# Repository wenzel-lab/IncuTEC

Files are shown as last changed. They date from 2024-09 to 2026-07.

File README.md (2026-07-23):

# IncuTEC

IncuTEC is a custom microscope incubator that uses a thermoelectric
(Peltier) heating and cooling system with CO₂ control. It is designed for
the [SQUID microscope](https://github.com/wenzel-lab/SQUID-bioimaging-platform)
and other optical instruments with a similar footprint.

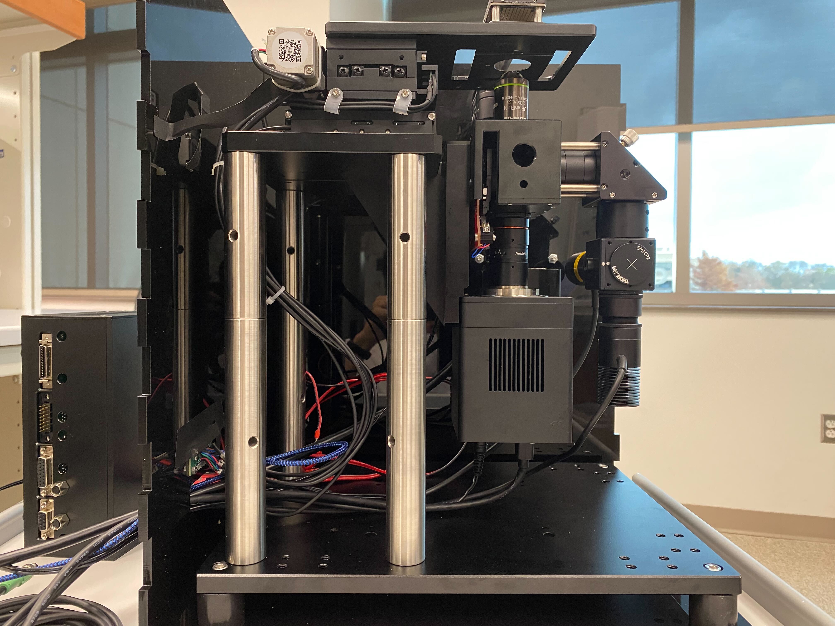
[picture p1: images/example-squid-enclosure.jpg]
IncuTEC enclosure around a SQUID microscope


## Documentation

### Start here

| Document | What it contains |
| --- | --- |
| [Assembly guide](assembly-guide.md) | Illustrated, step-by-step enclosure assembly instructions |
| [Bilingual assembly instructions (Word)](docs/incutec-assembly-instructions-bilingual.docx) | Spanish and English assembly instructions in a downloadable document |
| [Pneumatic system diagram](docs/incutec-pneumatic-system-diagram.pdf) | CO₂ tank, regulator, valves, gauges, and incubator connections |
| [UIM V2 user manual (English)](docs/uim-v2-user-manual-en.pdf) | Operation and configuration of the temperature controller display |
| [Temperature control module FAQ (English)](docs/tcm-temperature-control-module-faq-en.pdf) | Initial configuration and troubleshooting for the TCM controller |
| [UIM display module notes](docs/uim-display-module-notes.md) | Project-specific notes about language and maximum output voltage |

### Temperature-control references

- [TCM temperature control module overview (English)](docs/tcm-temperature-control-module-overview-en.pdf)
- [UIM universal display module overview (English)](docs/uim-universal-display-module-overview-en.pdf)
- [TCM parallel operation application note (English)](docs/tcm-parallel-operation-application-note-en.pdf)
- [Alternate translation of the TCM parallel operation application note](docs/tcm-parallel-operation-application-note-en-alternate.pdf)
- [Laird: heating and cooling of incubator chambers (2020)](docs/laird-incubator-heating-cooling-application-note-2020.pdf)
- [Laird SAA-170-24-22 thermoelectric cooler datasheet](docs/laird-saa-170-24-22-tec-datasheet.pdf)

### Sensor datasheets

- [Sensirion SCD30 CO₂, humidity, and temperature sensor](docs/SensorDatasheets/sensirion-scd30-co2-sensor-datasheet.pdf)
- [Winsen ME2-O2 oxygen sensor](docs/SensorDatasheets/winsen-me2-o2-sensor-manual.pdf)
- [Seeed Grove SHT35 temperature and humidity sensor](docs/SensorDatasheets/seeed-grove-sht35-temperature-humidity-sensor-datasheet.pdf)
- [Seeed Grove MQ2 gas sensor](docs/SensorDatasheets/seeed-grove-mq2-gas-sensor-datasheet.pdf)
- [Seeed Grove light sensor v1.2](docs/SensorDatasheets/seeed-grove-light-sensor-v1.2-datasheet.pdf)
- [Seeed Grove real-time clock](docs/SensorDatasheets/seeed-grove-rtc-user-manual.pdf)

## Wenzel Lab operating guide

> [!CAUTION]
> CO₂ can displace oxygen. Use the incubator only in a properly ventilated
> space, secure the gas cylinder, and follow your institution's compressed-gas
> safety procedures.

### Start-up

1. Check that the pneumatic connections are secure and that the run/vent valve
   on the incubator is in the correct position.
2. Switch on the mains power at the back of the controller. The Raman laser
   driver is powered by the same controller/power supply.
3. Set the target temperature and switch temperature control on using the UIM
   display (the white box with the round button).
4. Open the main valve on the CO₂ cylinder.
5. Move the gas-control slider on the controller to **HIGH**. The target CO₂
   percentage can currently be changed only in the microcontroller settings
   over USB.
6. Monitor temperature and CO₂ until both readings are stable before beginning
   an experiment.

### Shut-down

1. Close the main valve on the CO₂ cylinder; the regulator does not need to be
   adjusted.
2. Vent the remaining CO₂ using the run/vent valve near the incubator inlet.
3. Move the gas-control slider to **LOW**.
4. Switch temperature control off using the UIM display.
5. Turn off the main power-supply switch.

## Project resources

- [3D models](3DModels/)
- [Control electronics, code, and schematics](control/)
- [Assembly images](images/AssemblyImages/)
- [SQUID inverted microscope enclosure example](https://forum.squid-imaging.org/t/assembly-guide-for-inverted-system-with-the-60-mm-x-60-mm-stage/51)

## Design overview

The chamber consists of two self-sealing parts: a bottom section that
accommodates the microscope feet and cables, and a removable top section that
seals against the base. The target operating range is approximately 4–40 °C,
with 37 °C as the typical setpoint. The current gas system adds CO₂ to ambient
air for mammalian cell culture and microaerobic applications; the design is
intended to remain extensible toward anaerobic operation.

The temperature-control assembly is inspired by incubator designs from the
Prakash Lab and adapted for additional uses and gas control.

## Bill of materials highlights

- [Yexian TCM Standard temperature controller](http://yexian.com/product/tcm_standard.htm)
  with PID auto-tuning
- [Laird SAA-170-24-22 air-to-air thermoelectric cooler](https://www.mouser.cl/ProductDetail/Laird-Thermal-Systems/387000612?qs=uwxL4vQweFP51dqtRIyGCw%3D%3D)
- Acrylic sheet or rigid insulating foam for the enclosure

## Open items

- Characterize the temperature ramp speed for 12 V and 24 V controller supply
  configurations.
- Validate the achievable CO₂ control range around the 5% setpoint.
- Install an independent room CO₂ monitor.

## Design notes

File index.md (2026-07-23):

# IncuTEC microscope incubator

IncuTEC enclosure around a SQUID microscope

IncuTEC is a custom thermoelectric microscope incubator with CO₂ control.

## Quick links

- [Assembly guide](assembly-guide.md)
- [Operating guide and complete documentation index](README.md)
- [Pneumatic system diagram](docs/incutec-pneumatic-system-diagram.pdf)
- [UIM V2 temperature controller manual](docs/uim-v2-user-manual-en.pdf)
- [Temperature controller FAQ](docs/tcm-temperature-control-module-faq-en.pdf)

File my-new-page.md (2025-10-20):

[M4x10 screws]:Parts.yaml#M4x10PanSteel
[No. 2 Phillips screwdriver]:Parts.yaml#Screwdriver_Philips_No2
# Assembly Instructions

{{BOM}}

## Gluing and sealing walls {pagestep}

Position the plates accordingly, ensuring a 90° angle between them. Using the [syringe]{qty:1, cat:tool}, inject the [acrylic adhesive liquid]{qty:some, cat:tool} between the plates you want to join, waiting for it to bond before moving on to the next plate. Once all the plates are bonded, use a [rod][glass rod]{qty:1, cat:tool} to add the previously diluted acrylic to each of the joints. Ensure that the mixture covers each section of the joints to prevent leaks. Parts: [Base](3DModels/Base.stl){qty:1}{previewpage}, [Base back](3DModels/BaseBack.stl){qty:1}{previewpage}, [Base front](3DModels/BaseFront.stl){qty:1}{previewpage}, [Base side 1](3DModels/BaseSide1.stl){qty:1}{previewpage}, [Base side 2](3DModels/BaseSide2.stl){qty:1}{previewpage}, [Cover](3DModels/Cover.stl){qty:1}{previewpage}, [Cover side 1](3DModels/CoverSide1.stl){qty:1}{previewpage}, [Cover side 2](3DModels/CoverSide2.stl){qty:1}{previewpage}, [Cover back](3DModels/CoverFrontBack.stl){qty:2}{previewpage}, [Seal frame](3DModels/SealFrame.stl){qty:2}{previewpage}.

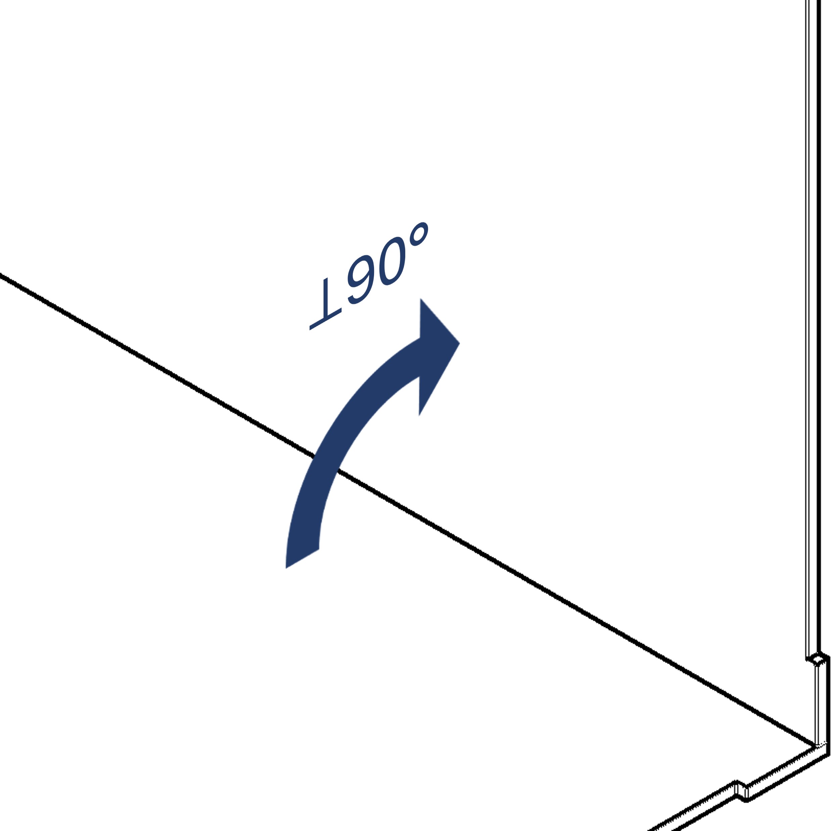
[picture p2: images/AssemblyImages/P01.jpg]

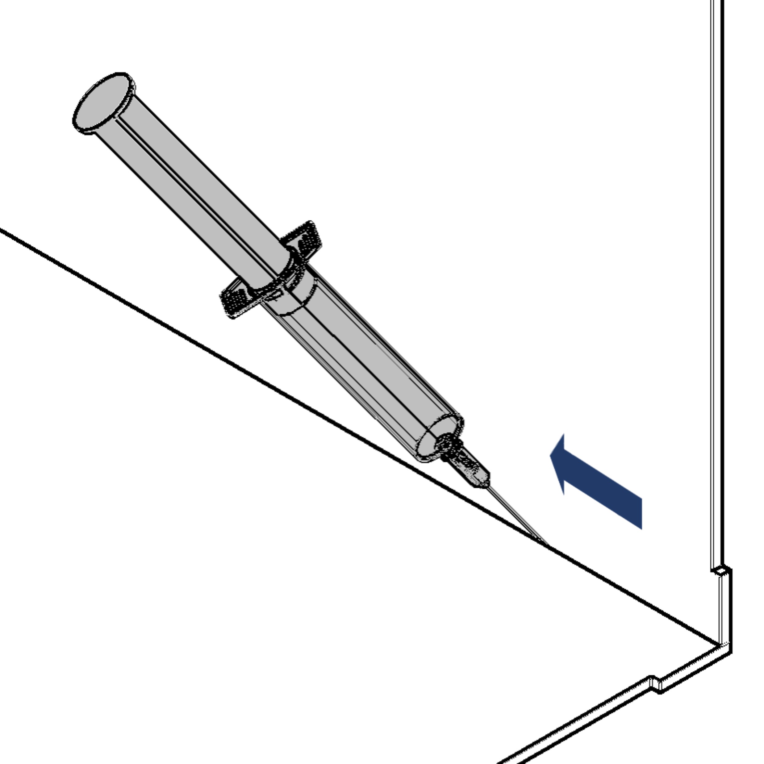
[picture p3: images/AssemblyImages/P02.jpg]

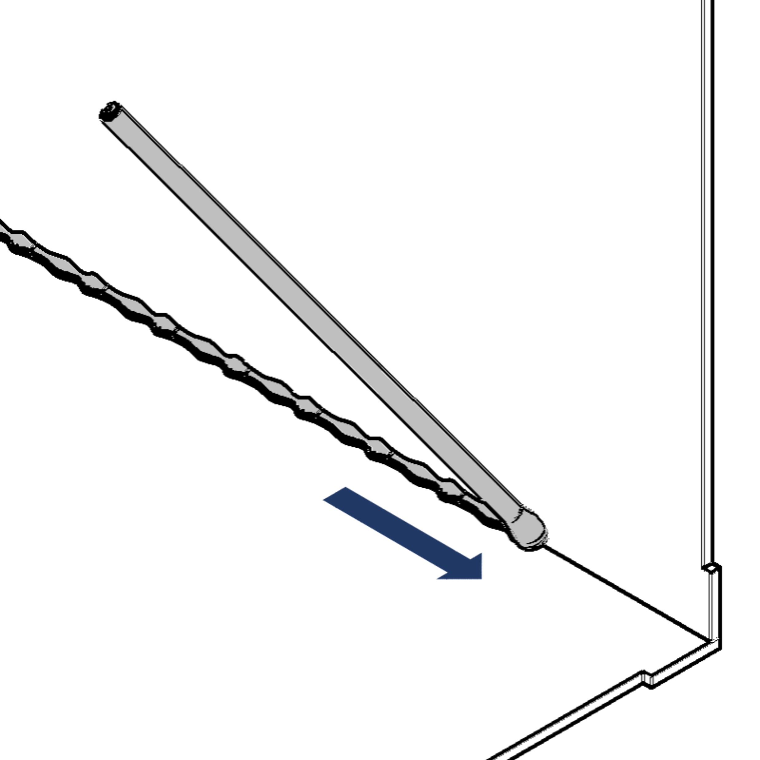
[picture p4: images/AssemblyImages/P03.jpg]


## Preparation of the screw cubes {pagestep}
Place the [M4][M4 nut]{qty:6}, [M5][M5 nut]{qty:14} and [M6][M6 nut]{qty:6} nuts in the hexagonal holes according to the hole dimensions. Using a [syringe], inject [resin][UV resin]{qty:some,cat:tool} into the three notches for each nut. Apply [UV light][UV flashlight]{qty:1, cat:tool} to cure the resin and secure the nuts in place.  Parts: [Screw cube 4 mm](3DModels/ScrewCube_4mm.stl){qty:6}{previewpage}, [Screw cube 5 mm](3DModels/ScrewCube_5mm.stl){qty:4}{previewpage}, [Screw cube 6 mm](3DModels/ScrewCube_6mm.stl){qty:6}{previewpage}, [Screw cube lock 1](3DModels/ScrewCubeLock1.stl){qty:2}{previewpage}, [Screw cube lock 2](3DModels/ScrewCubeLock2.stl){qty:2}{previewpage}.

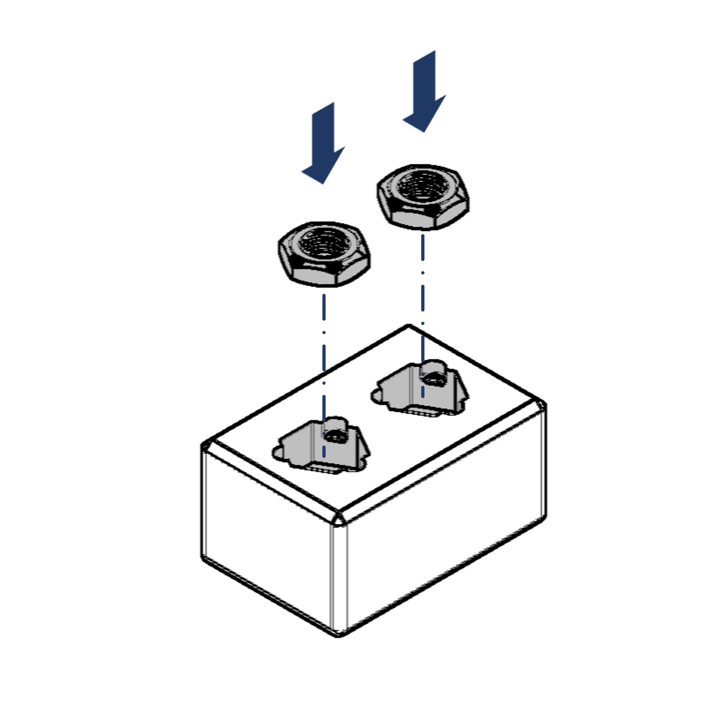
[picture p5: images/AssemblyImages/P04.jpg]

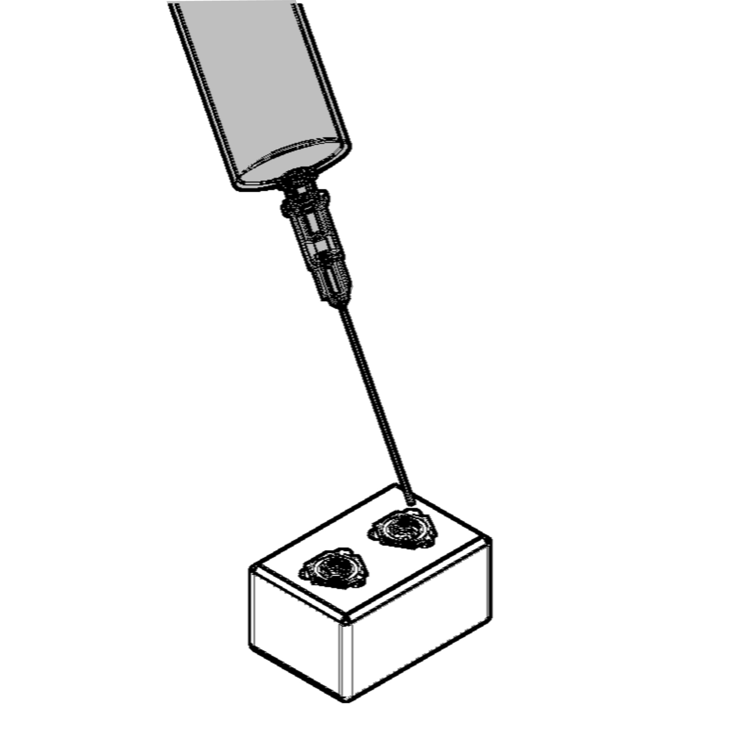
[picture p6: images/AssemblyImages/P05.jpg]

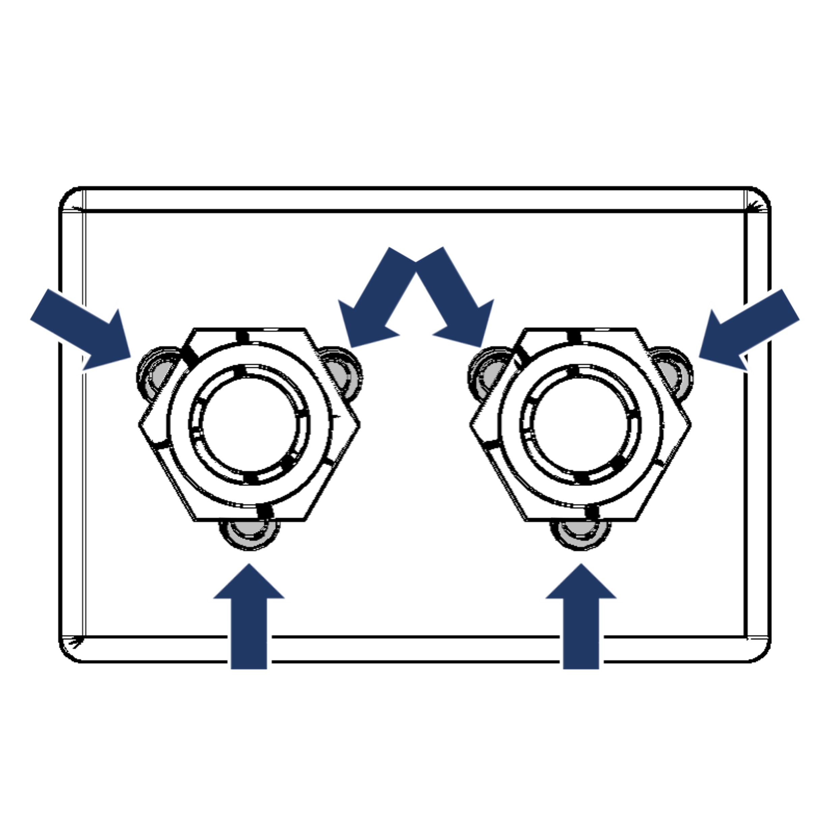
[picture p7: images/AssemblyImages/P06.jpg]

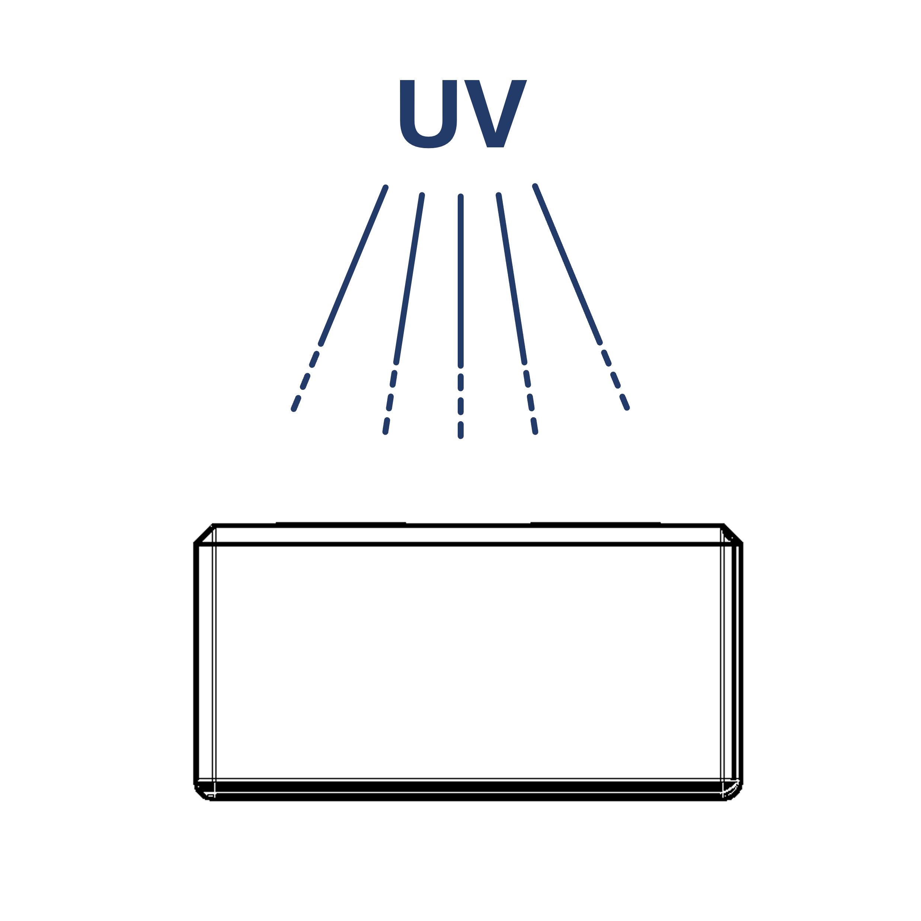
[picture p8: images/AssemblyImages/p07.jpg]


>! Be careful that the resin applied is only injected into the indicated notches. Avoid using excess resin that could affect the nut thread.

## Gluing the screw cubes {pagestep}
Apply [glue]{qty: some, cat:tool} suitable for gluing screw cubes to acrylic walls (such as cyanoacrylate). Cover the contact surface so that the product does not affect the nuts. Position the block in the correct place, applying pressure while gluing it properly. Parts: [Screw cube 4 mm], [Screw cube 5 mm], [Screw cube 6 mm], [Screw cube lock 1], [Screw cube lock 2], [Gas cube](3DModels/GasCube.stl){qty:1}{previewpage}

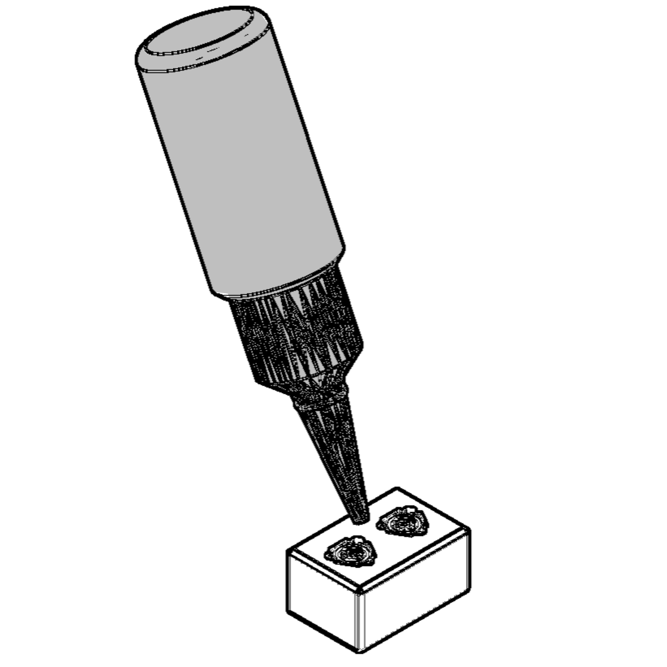
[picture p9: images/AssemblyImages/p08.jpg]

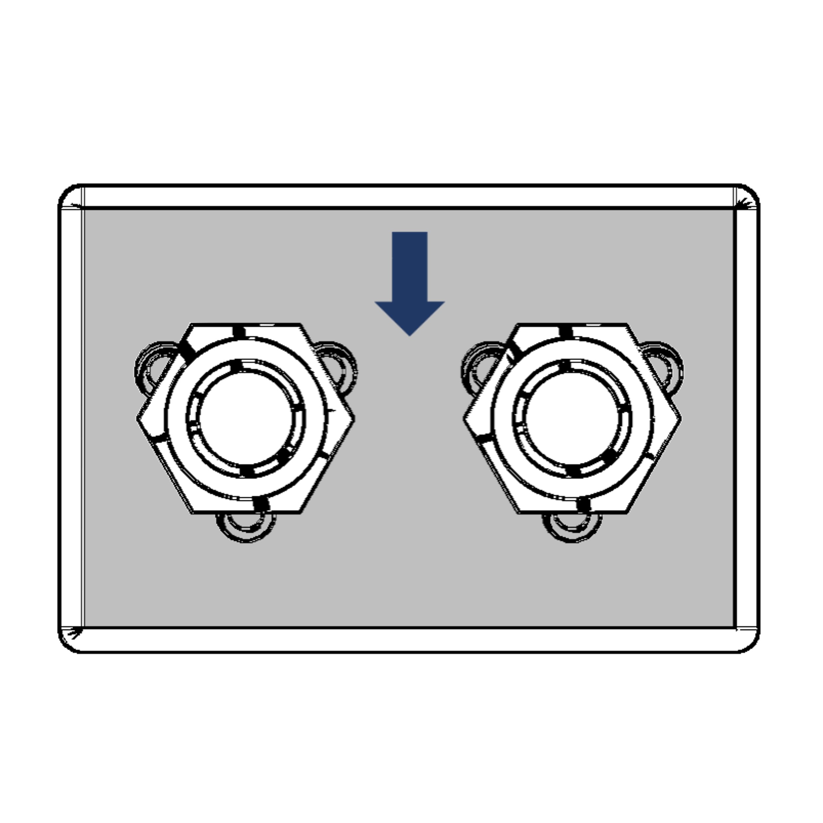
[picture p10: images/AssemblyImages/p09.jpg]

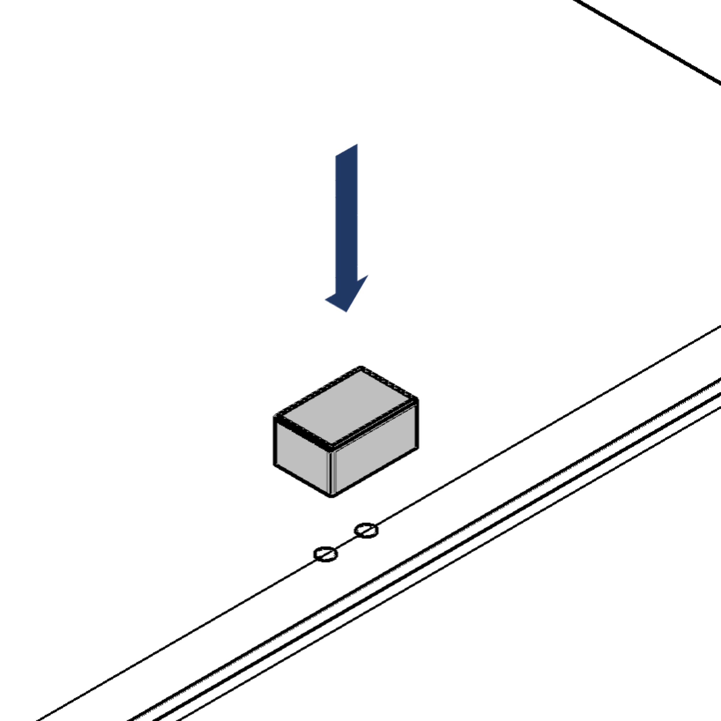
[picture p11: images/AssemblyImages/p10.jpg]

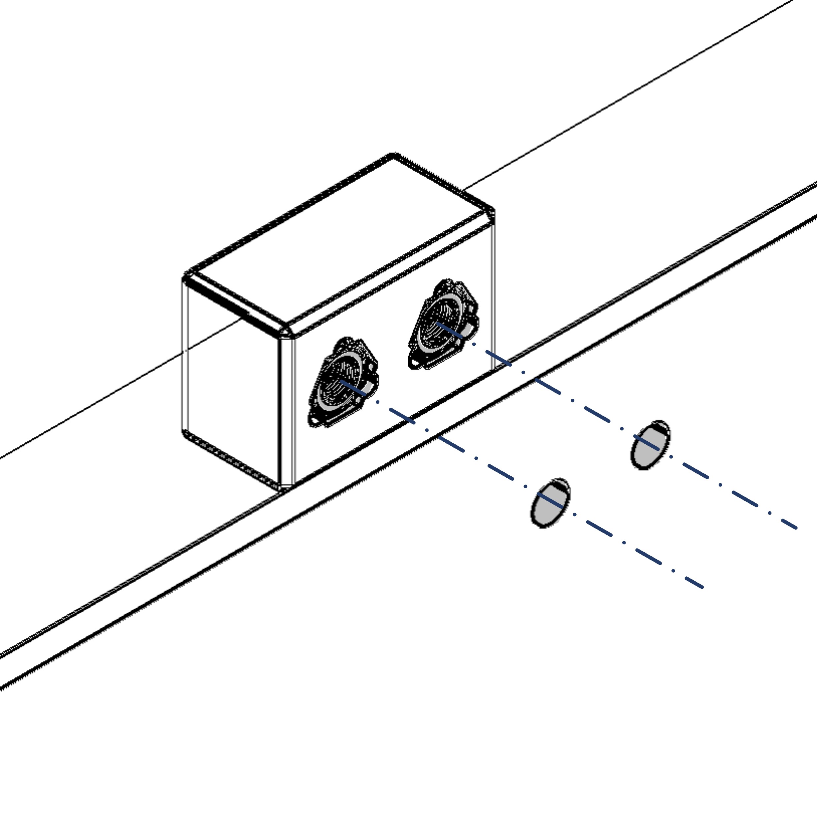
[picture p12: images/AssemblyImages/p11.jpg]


>! Ensure that the holes in the walls match the axis of the nuts so that the fixing bolts fit properly.

## Sealing screw cubes and other attached parts {pagestep}
Using a [syringe], apply [resin][UV resin] around the perimeter of the screw cube so that the product is visible continuously. Apply [UV light][UV flashlight] to cure the resin, ensuring that every part of the joint is covered.

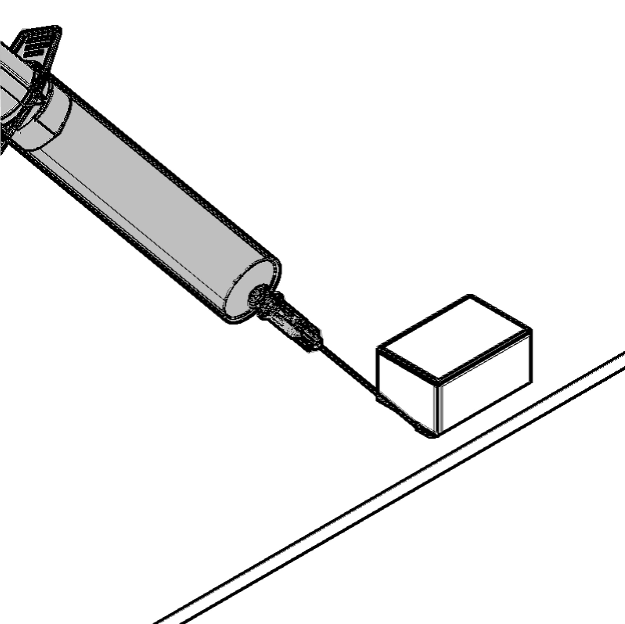
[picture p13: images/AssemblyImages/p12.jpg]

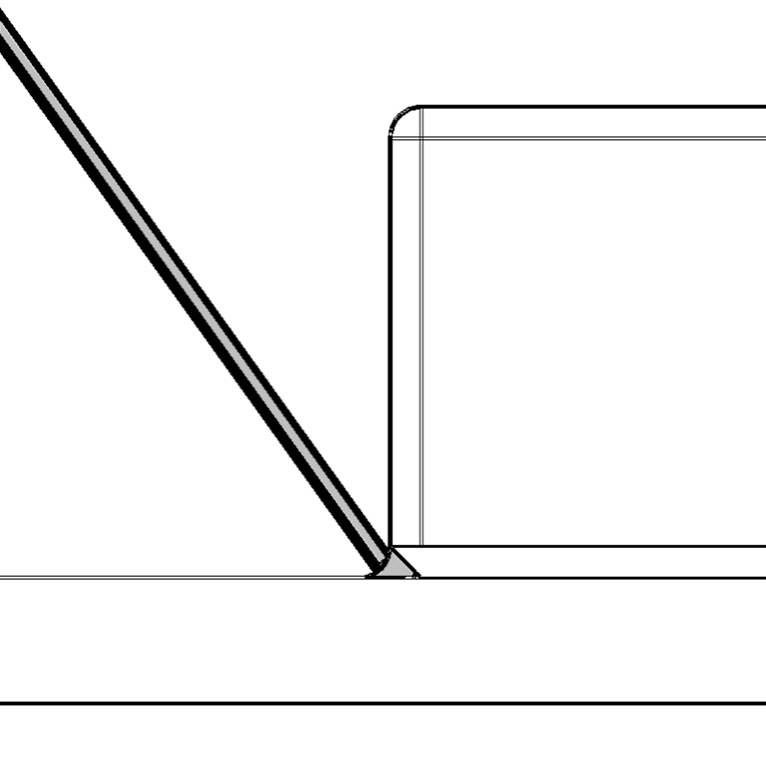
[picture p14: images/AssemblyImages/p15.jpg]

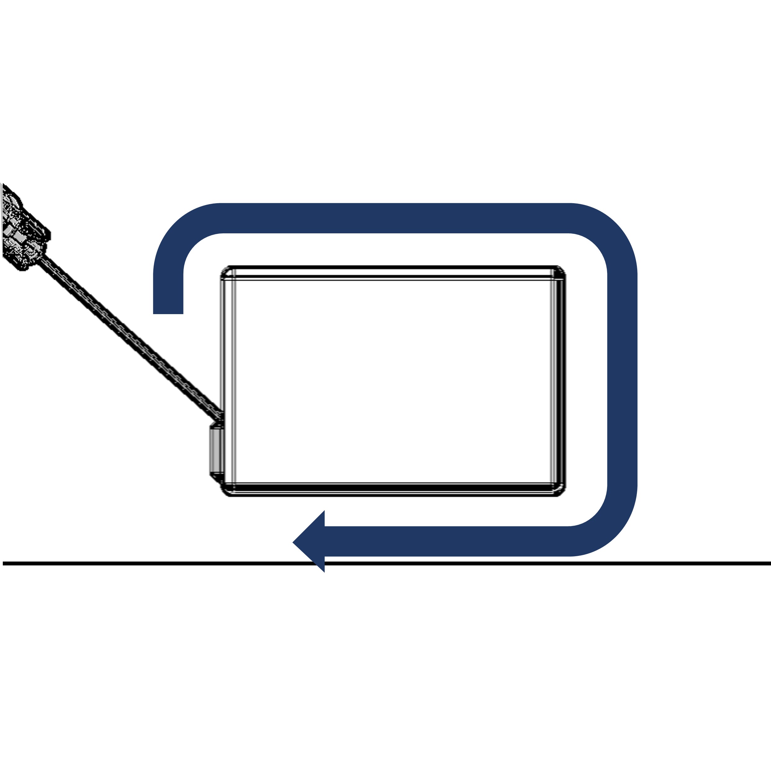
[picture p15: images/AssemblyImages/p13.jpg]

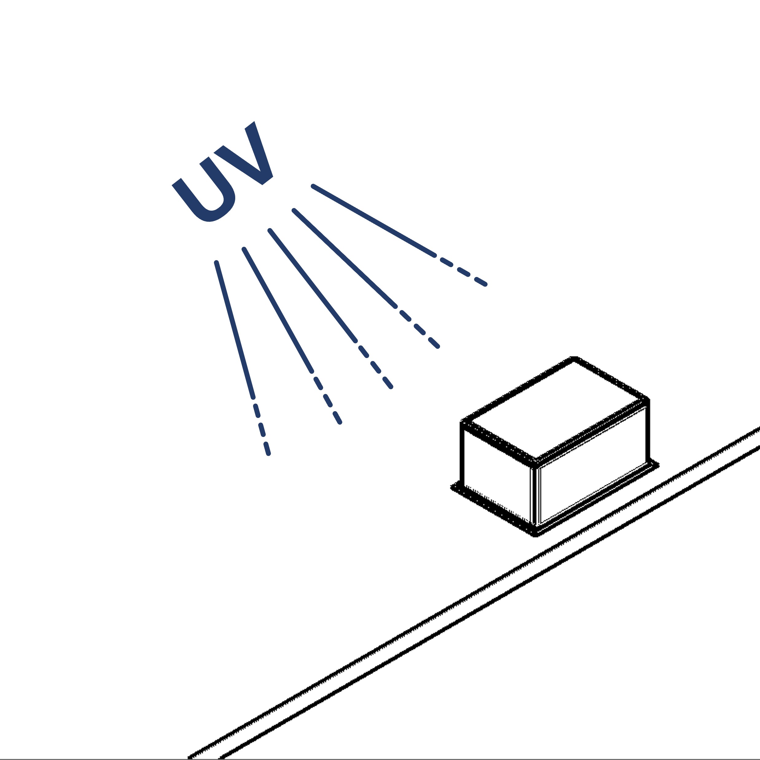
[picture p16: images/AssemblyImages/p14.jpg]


>! The resin will accumulate in the chamfer of the block by capillary action. Apply a sufficient but moderate amount to ensure proper sealing.

## Positioning of peripheral elements. {pagestep}
Place the different elements in their corresponding positions and secure them with the appropriate bolts ([M4][M4 bolt]{qty:6}, [M5][M5 bolt]{qty:14}, and [M6][M6 bolt]{qty:6}).

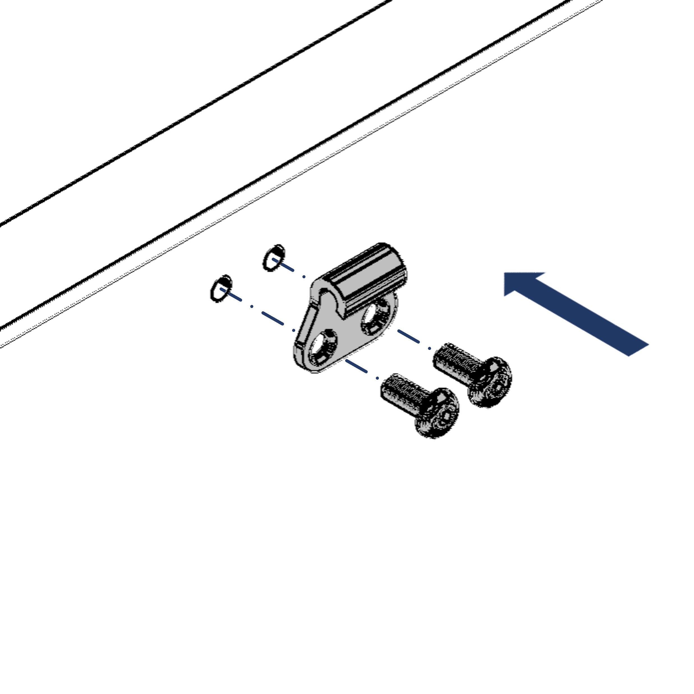
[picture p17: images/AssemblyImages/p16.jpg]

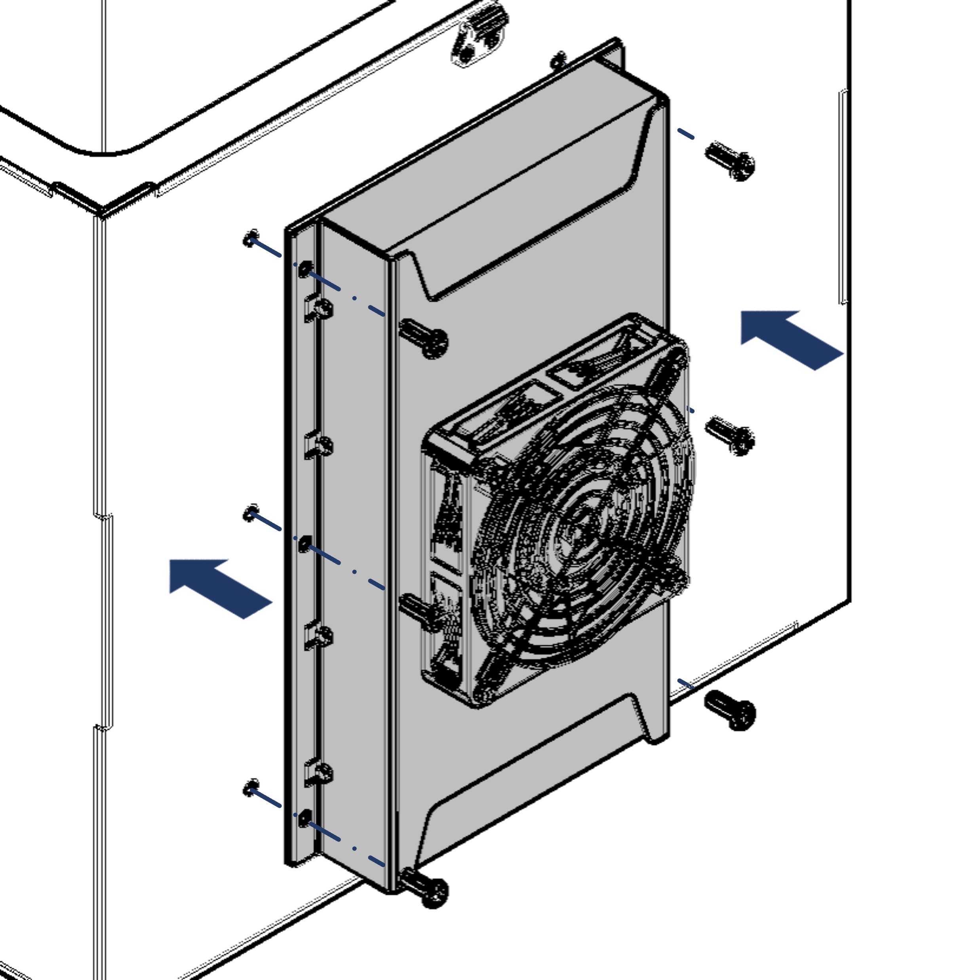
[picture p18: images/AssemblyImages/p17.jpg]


## Preparation and installation of cables {pagestep}
Using a [sharp tool][scalpel]{qty:1,cat:tool}, make cuts in the cable pass-through rubber for each of the cables that will enter the incubator. Pass each cable through the rubber. Mount the rubber with the corresponding frame and tighten the bolts.

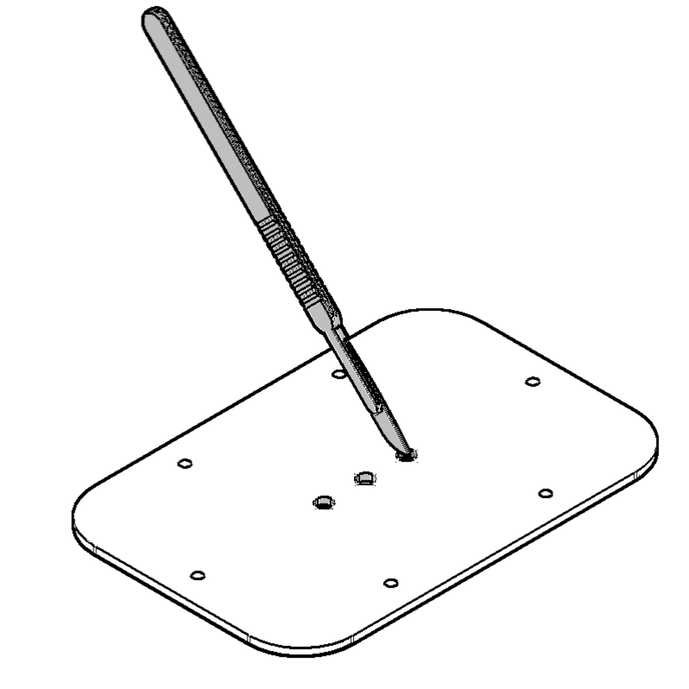
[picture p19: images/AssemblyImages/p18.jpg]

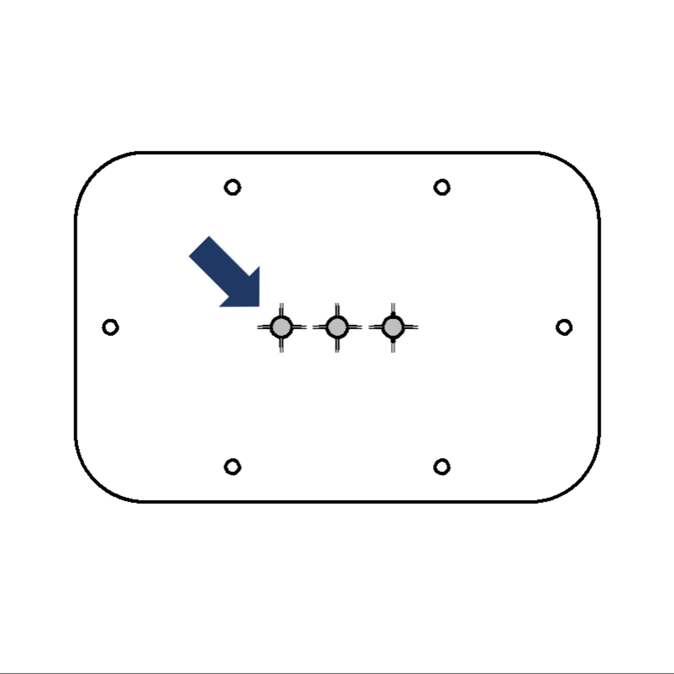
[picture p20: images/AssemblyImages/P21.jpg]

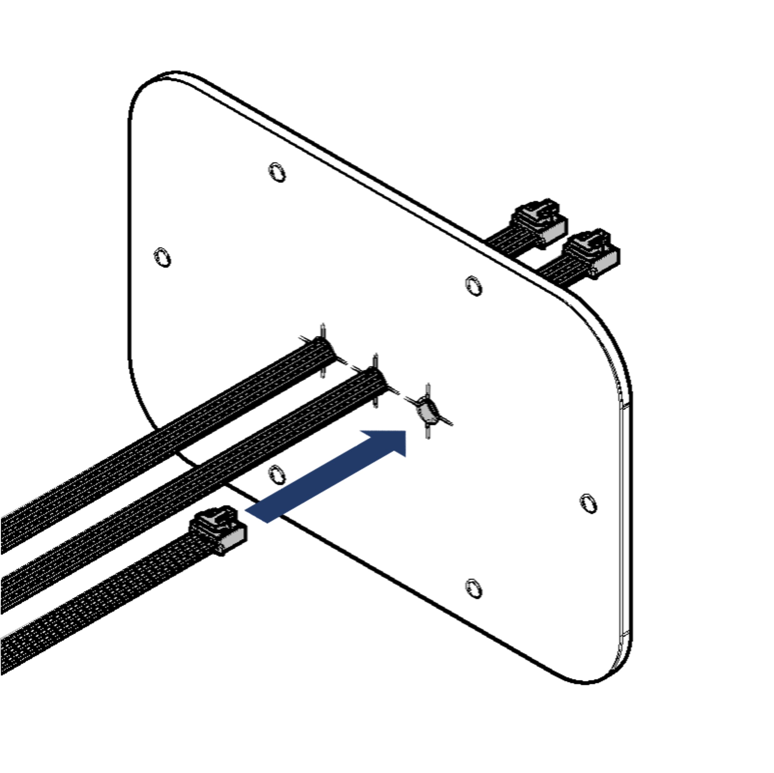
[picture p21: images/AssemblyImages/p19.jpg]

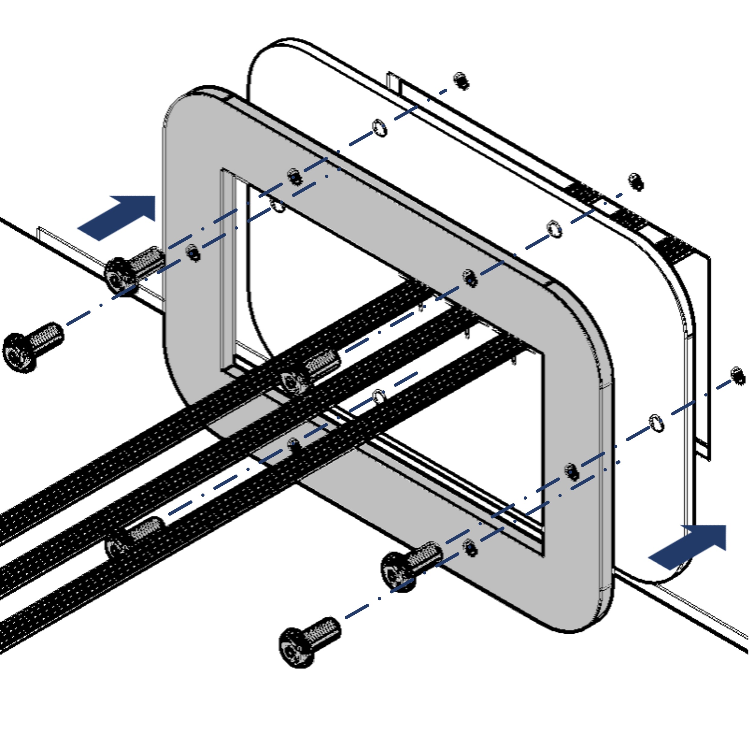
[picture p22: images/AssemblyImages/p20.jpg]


>! The cuts for the cables must be made in such a way that each cable is surrounded by rubber. Two perpendicular cuts must be added to allow the connectors attached to each cable to pass through.

## Closing the incubator {pagestep}
Place the [rubber gasket]{qty:1} on the frame of the incubator base. Place the lid on the gasket and close the incubator using the quick-release clamps.

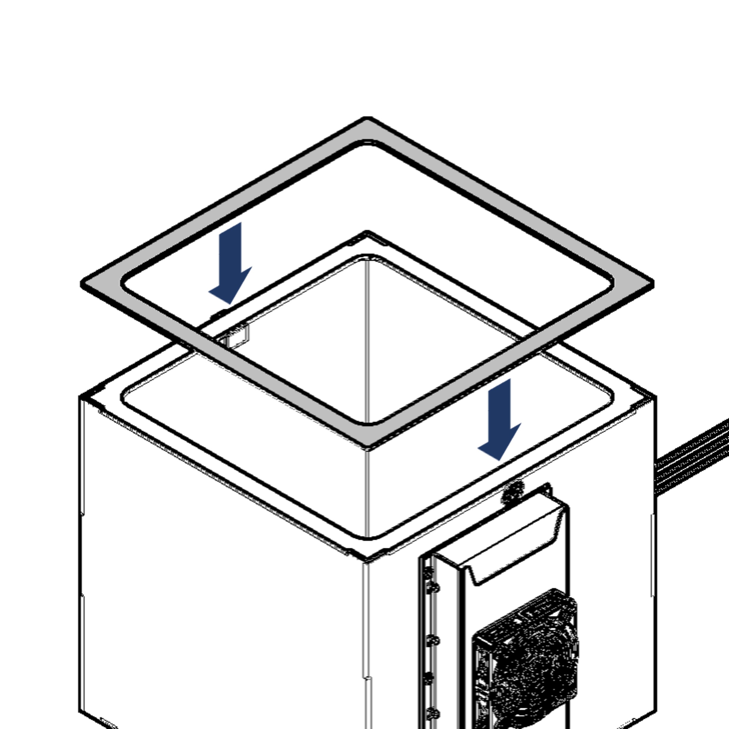
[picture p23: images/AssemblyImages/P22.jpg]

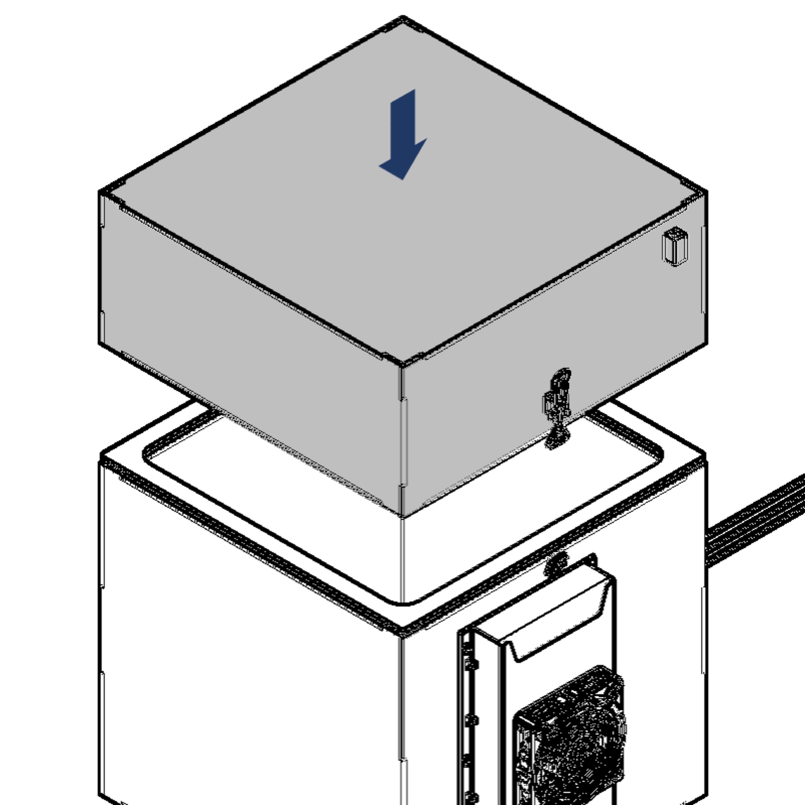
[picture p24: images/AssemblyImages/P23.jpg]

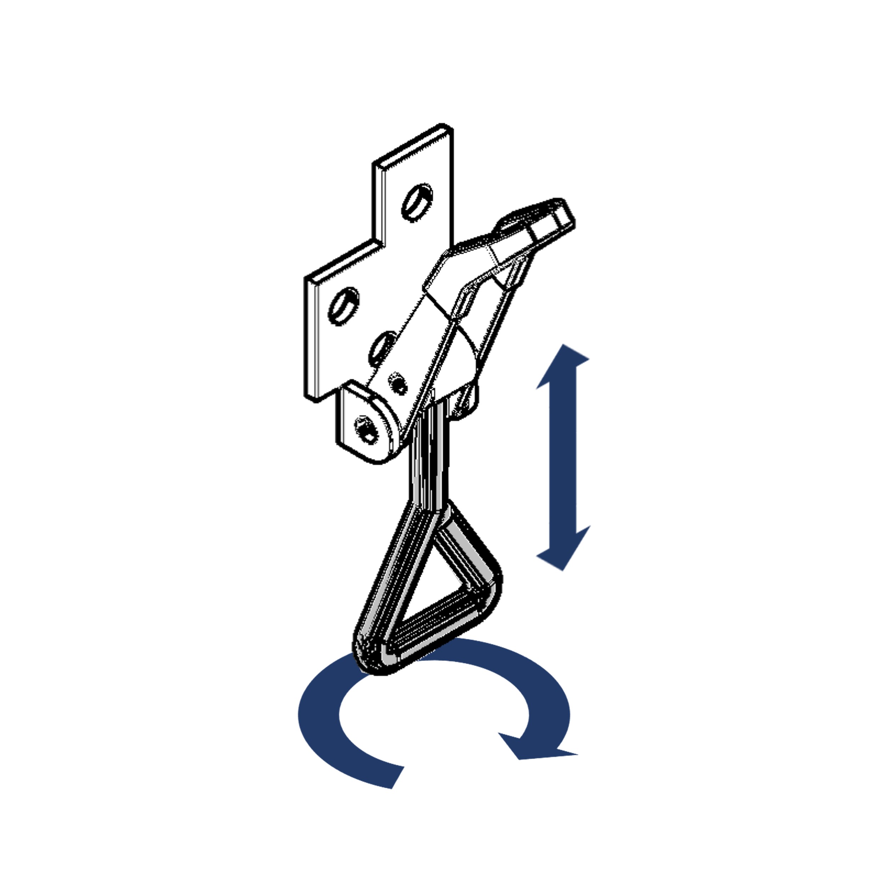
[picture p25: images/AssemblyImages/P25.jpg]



>! Adjust the length of the clamp by turning it until you achieve a length that allows the incubator to be closed without excessive tension.

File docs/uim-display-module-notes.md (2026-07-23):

# UIM display module notes

- Switch the controller output **off** before changing the maximum output
  voltage. The setting cannot be changed while the output is active.
- To change the interface language from Chinese to English, open
  **SYSTEM → General Information**.

See the [UIM V2 user manual](uim-v2-user-manual-en.pdf) for complete operating
instructions.

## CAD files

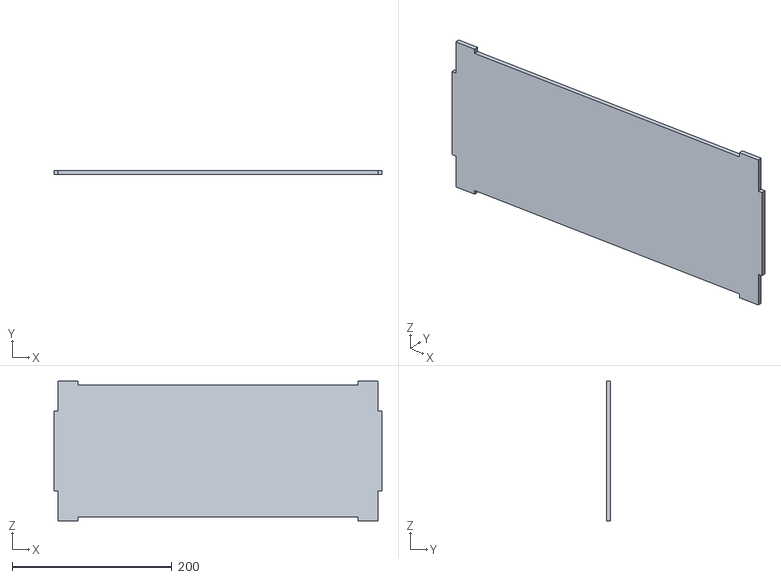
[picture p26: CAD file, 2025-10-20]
3DModels/CoverFrontBack.stl
410.0 x 5.00 x 174.5

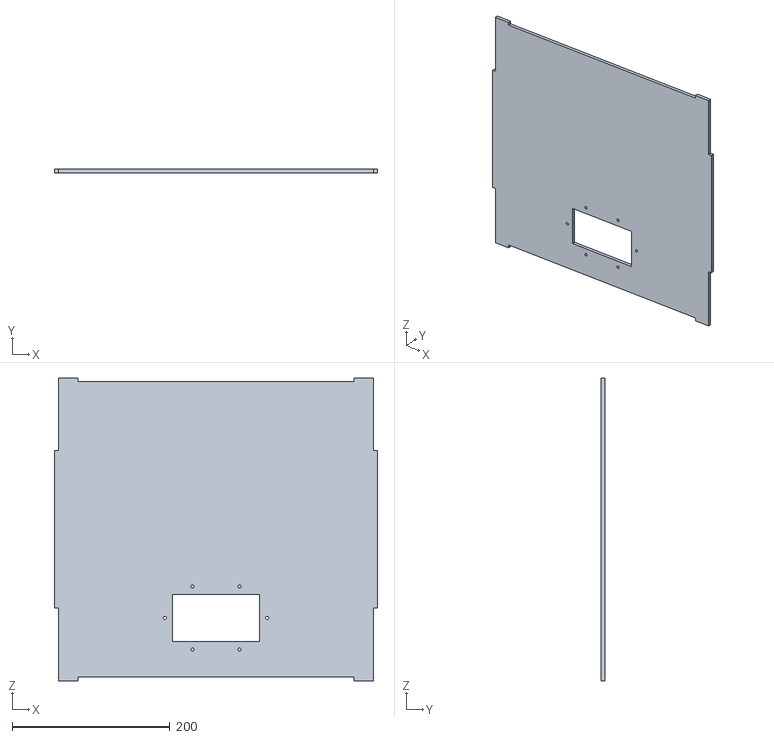
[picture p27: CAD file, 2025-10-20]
3DModels/BaseBack.stl
410.0 x 5.00 x 384.5

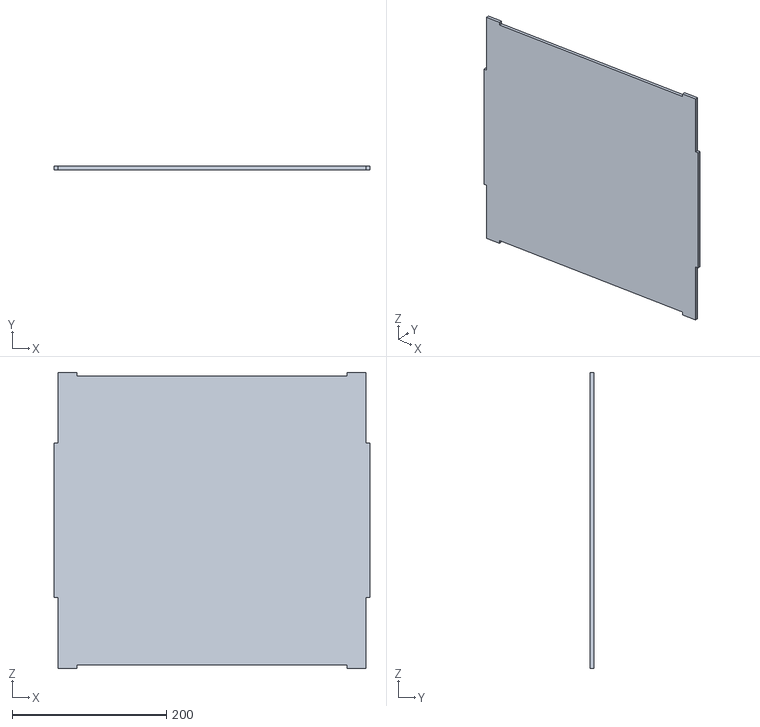
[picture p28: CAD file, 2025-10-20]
3DModels/BaseFront.stl
410.0 x 5.00 x 384.5

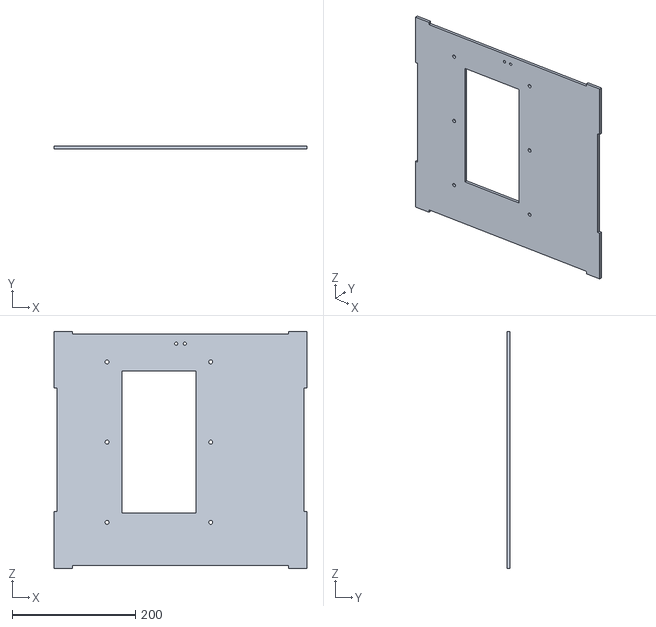
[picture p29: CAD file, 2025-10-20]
3DModels/BaseSide1.stl
410.0 x 5.00 x 384.5

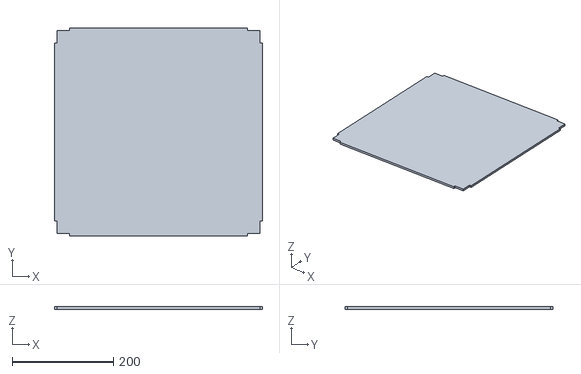
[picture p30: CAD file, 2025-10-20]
3DModels/Base.stl
410.0 x 410.0 x 5.00

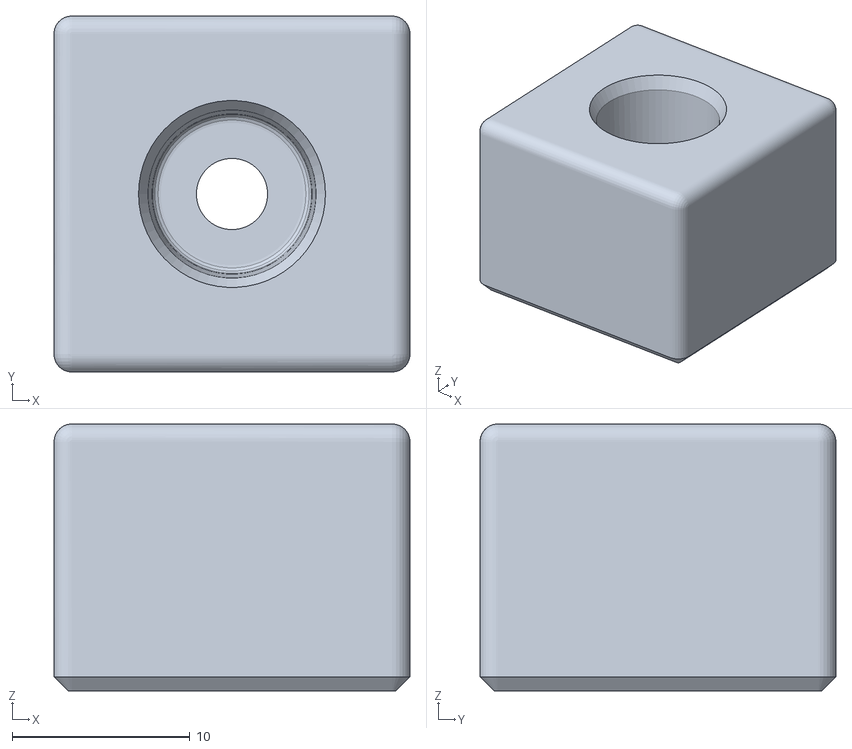
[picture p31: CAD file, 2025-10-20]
3DModels/GasCube.stl
20.0 x 20.0 x 15.0

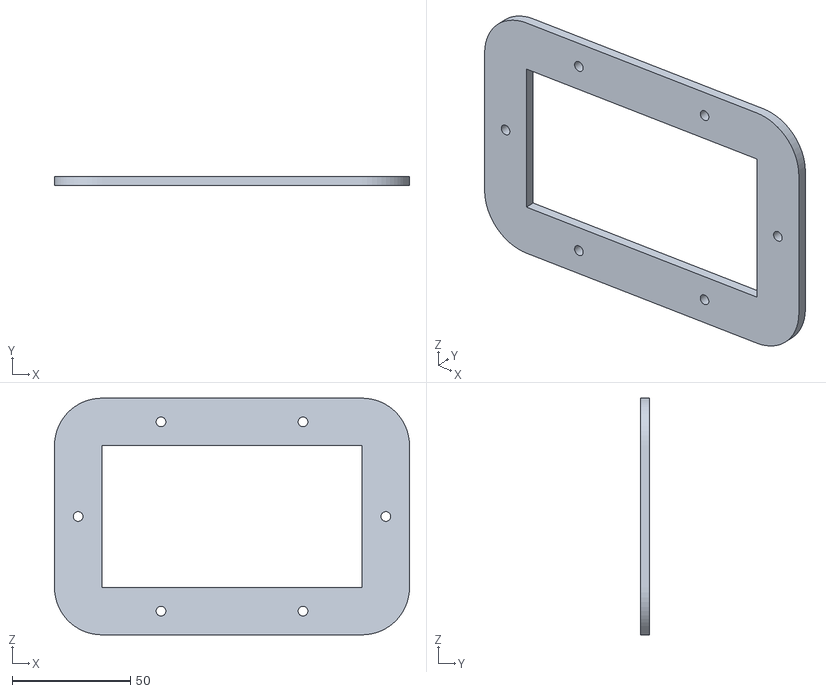
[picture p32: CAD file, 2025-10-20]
3DModels/CableFrame.stl
150.0 x 4.00 x 100.0

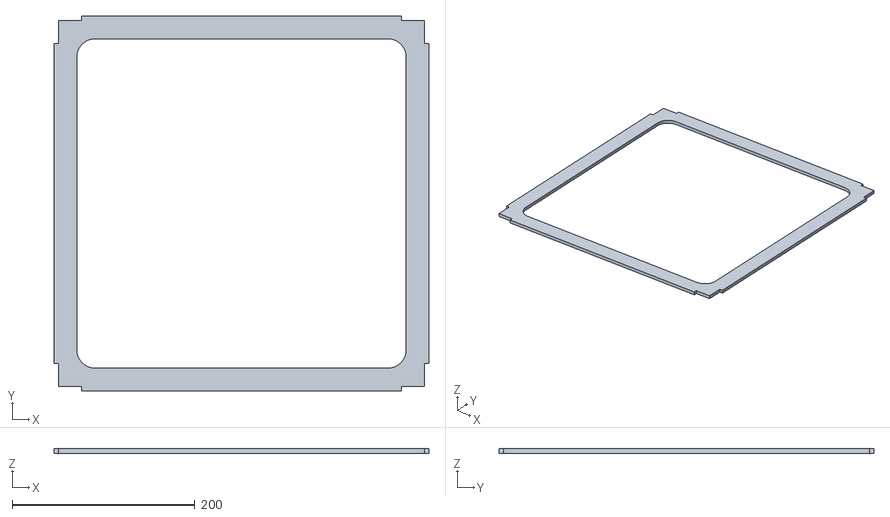
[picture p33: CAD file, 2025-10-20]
3DModels/SealFrame.stl
410.0 x 410.0 x 5.00

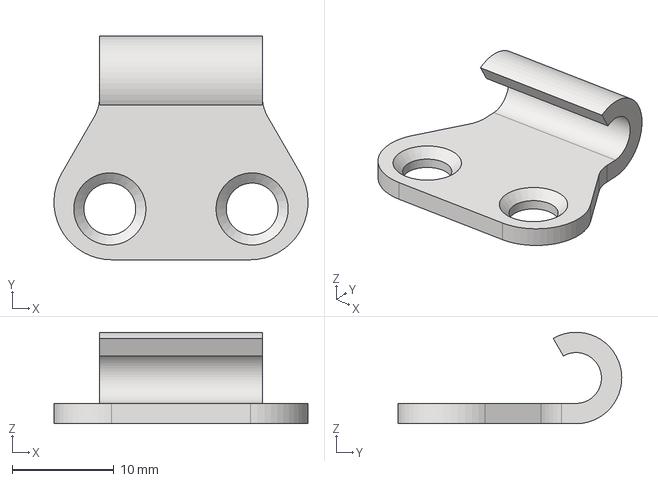
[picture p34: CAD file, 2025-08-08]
3DModels/IncubatorPart27.step
25.0 x 22.0 x 9.00 mm

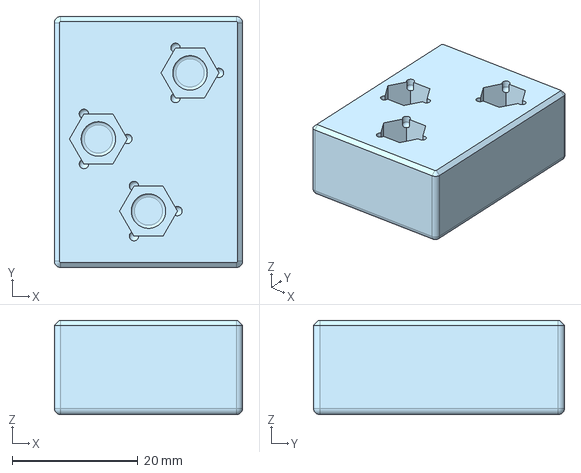
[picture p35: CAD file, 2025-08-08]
3DModels/IncubatorPart12.step
30.0 x 40.0 x 15.0 mm

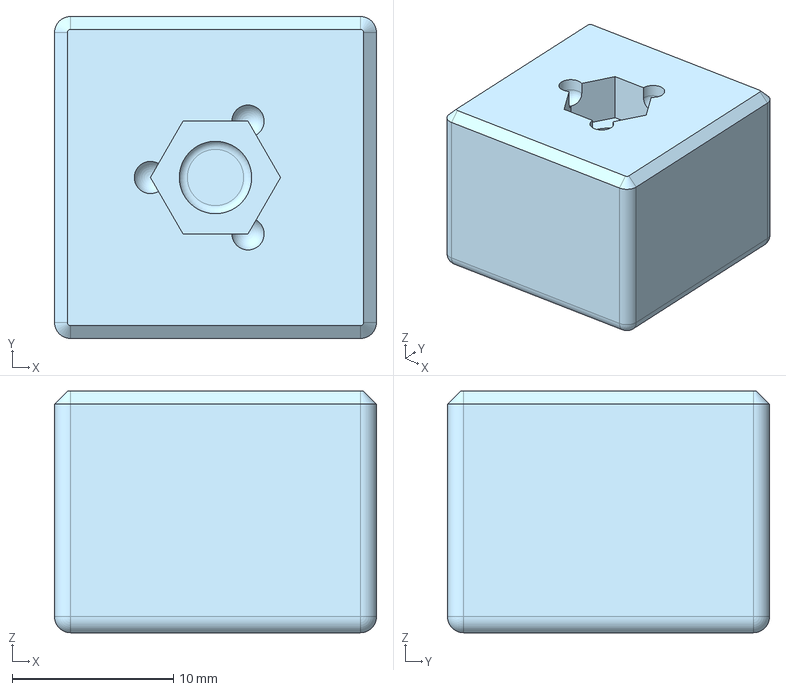
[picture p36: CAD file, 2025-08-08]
3DModels/IncubatorPart4.step
20.0 x 20.0 x 15.0 mm

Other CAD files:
3DModels/BaseSide2.stl
3DModels/CoverSide2.stl
3DModels/CoverSide1.stl
3DModels/IncubatorPart34.step
3DModels/IncubatorPart19.step
3DModels/IncubatorPart14.step
3DModels/IncubatorPart0.step
3DModels/IncubatorPart1.step
3DModels/IncubatorPart10.step
3DModels/IncubatorPart11.step
3DModels/IncubatorPart13.step
3DModels/IncubatorPart15.step
3DModels/IncubatorPart16.step
3DModels/IncubatorPart17.step
3DModels/IncubatorPart18.step
3DModels/IncubatorPart2.step
3DModels/IncubatorPart20.step
3DModels/IncubatorPart21.step
3DModels/IncubatorPart22.step
3DModels/IncubatorPart23.step
3DModels/IncubatorPart24.step
3DModels/IncubatorPart25.step
3DModels/IncubatorPart26.step
3DModels/IncubatorPart28.step
3DModels/IncubatorPart29.step
3DModels/IncubatorPart30.step
3DModels/IncubatorPart31.step
3DModels/IncubatorPart32.step
3DModels/IncubatorPart33.step
3DModels/IncubatorPart35.step
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

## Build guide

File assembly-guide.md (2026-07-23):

# IncuTEC assembly guide

[M4x10 screws]:Parts.yaml#M4x10PanSteel
[No. 2 Phillips screwdriver]:Parts.yaml#Screwdriver_Philips_No2

{{BOM}}

## Gluing and sealing walls {pagestep}

Position the plates accordingly, ensuring a 90° angle between them. Using the [syringe]{qty:1, cat:tool}, inject the [acrylic adhesive liquid]{qty:some, cat:tool} between the plates you want to join, waiting for it to bond before moving on to the next plate. Once all the plates are bonded, use a [rod][glass rod]{qty:1, cat:tool} to add the previously diluted acrylic to each of the joints. Ensure that the mixture covers each section of the joints to prevent leaks. Parts: [Base](3DModels/Base.stl){qty:1}{previewpage}, [Base back](3DModels/BaseBack.stl){qty:1}{previewpage}, [Base front](3DModels/BaseFront.stl){qty:1}{previewpage}, [Base side 1](3DModels/BaseSide1.stl){qty:1}{previewpage}, [Base side 2](3DModels/BaseSide2.stl){qty:1}{previewpage}, [Cover](3DModels/Cover.stl){qty:1}{previewpage}, [Cover side 1](3DModels/CoverSide1.stl){qty:1}{previewpage}, [Cover side 2](3DModels/CoverSide2.stl){qty:1}{previewpage}, [Cover back](3DModels/CoverFrontBack.stl){qty:2}{previewpage}, [Seal frame](3DModels/SealFrame.stl){qty:2}{previewpage}.





## Preparation of the screw cubes {pagestep}
Place the [M4][M4 nut]{qty:6}, [M5][M5 nut]{qty:14} and [M6][M6 nut]{qty:6} nuts in the hexagonal holes according to the hole dimensions. Using a [syringe], inject [resin][UV resin]{qty:some,cat:tool} into the three notches for each nut. Apply [UV light][UV flashlight]{qty:1, cat:tool} to cure the resin and secure the nuts in place.  Parts: [Screw cube 4 mm](3DModels/ScrewCube_4mm.stl){qty:6}{previewpage}, [Screw cube 5 mm](3DModels/ScrewCube_5mm.stl){qty:4}{previewpage}, [Screw cube 6 mm](3DModels/ScrewCube_6mm.stl){qty:6}{previewpage}, [Screw cube lock 1](3DModels/ScrewCubeLock1.stl){qty:2}{previewpage}, [Screw cube lock 2](3DModels/ScrewCubeLock2.stl){qty:2}{previewpage}.






>! Be careful that the resin applied is only injected into the indicated notches. Avoid using excess resin that could affect the nut thread.

## Gluing the screw cubes {pagestep}
Apply [glue]{qty: some, cat:tool} suitable for gluing screw cubes to acrylic walls (such as cyanoacrylate). Cover the contact surface so that the product does not affect the nuts. Position the block in the correct place, applying pressure while gluing it properly. Parts: [Screw cube 4 mm], [Screw cube 5 mm], [Screw cube 6 mm], [Screw cube lock 1], [Screw cube lock 2], [Gas cube](3DModels/GasCube.stl){qty:1}{previewpage}






>! Ensure that the holes in the walls match the axis of the nuts so that the fixing bolts fit properly.

## Sealing screw cubes and other attached parts {pagestep}
Using a [syringe], apply [resin][UV resin] around the perimeter of the screw cube so that the product is visible continuously. Apply [UV light][UV flashlight] to cure the resin, ensuring that every part of the joint is covered.






>! The resin will accumulate in the chamfer of the block by capillary action. Apply a sufficient but moderate amount to ensure proper sealing.

## Positioning of peripheral elements. {pagestep}
Place the different elements in their corresponding positions and secure them with the appropriate bolts ([M4][M4 bolt]{qty:6}, [M5][M5 bolt]{qty:14}, and [M6][M6 bolt]{qty:6}).




## Preparation and installation of cables {pagestep}
Using a [sharp tool][scalpel]{qty:1,cat:tool}, make cuts in the cable pass-through rubber for each of the cables that will enter the incubator. Pass each cable through the rubber. Mount the rubber with the corresponding frame and tighten the bolts.






>! The cuts for the cables must be made in such a way that each cable is surrounded by rubber. Two perpendicular cuts must be added to allow the connectors attached to each cable to pass through.

## Closing the incubator {pagestep}
Place the [rubber gasket]{qty:1} on the frame of the incubator base. Place the lid on the gasket and close the incubator using the quick-release clamps.




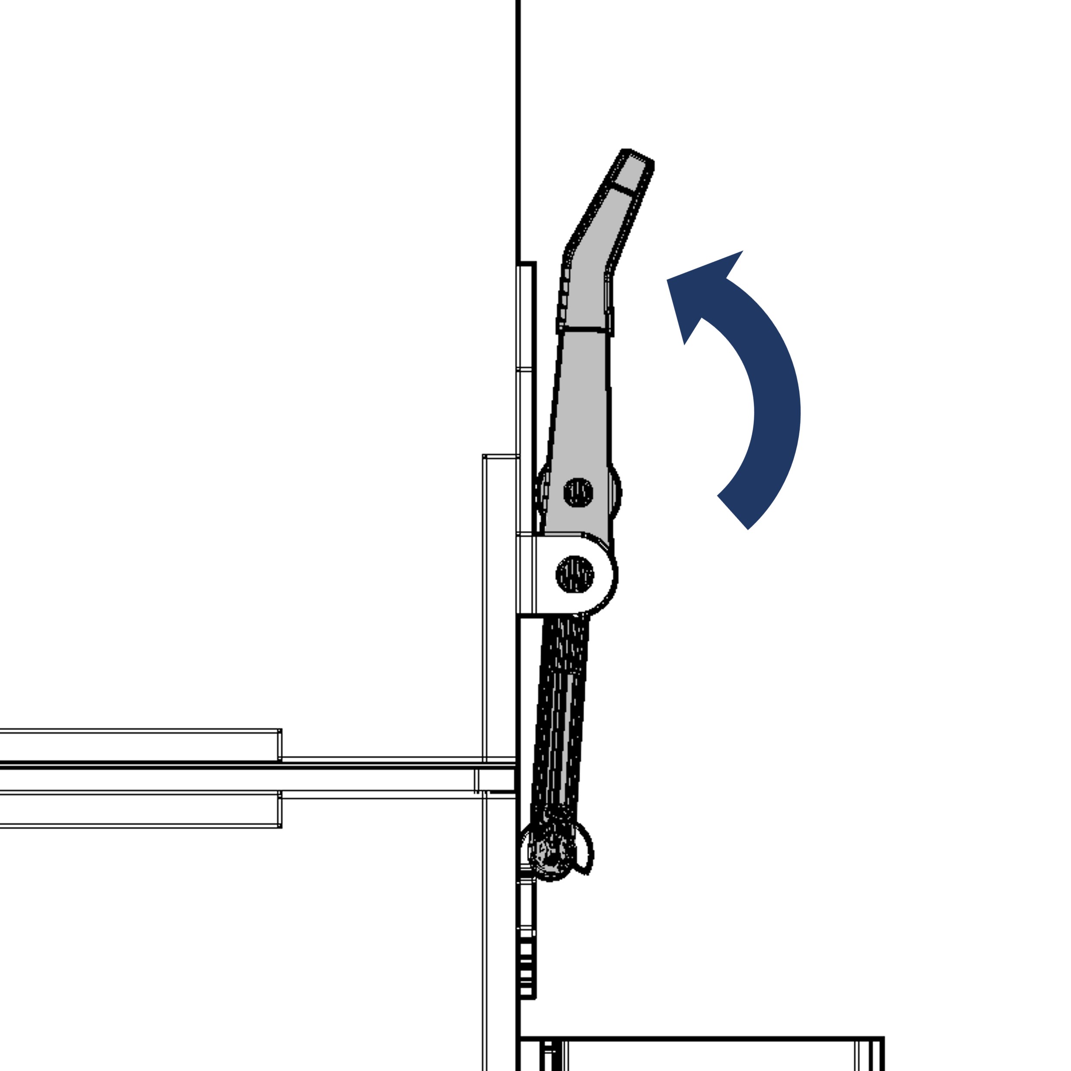
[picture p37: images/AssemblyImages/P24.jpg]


>! Adjust the length of the clamp by turning it until you achieve a length that allows the incubator to be closed without excessive tension.

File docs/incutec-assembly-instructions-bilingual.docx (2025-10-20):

| ES – Pegado y sellado de paredes. Posicione las placas según corresponda asegurando un ángulo de 90° entre ellas. Con la jeringa inyecte el líquido pegamento entre las placas que se quieran unir, procurando esperar que pegue para proceder a la siguiente placa. Una vez pegadas todas las placas, añada con una varilla el acrílico previamente diluido en cada una de las uniones. Asegúrese que la mezcla cubra cada sección de las uniones para evitar filtraciones.
| EN – Gluing and sealing walls. Position the plates accordingly, ensuring a 90° angle between them. Using the syringe, inject the adhesive liquid between the plates you want to join, waiting for it to bond before moving on to the next plate. Once all the plates are bonded, use a rod to add the previously diluted acrylic to each of the joints. Ensure that the mixture covers each section of the joints to prevent leaks.

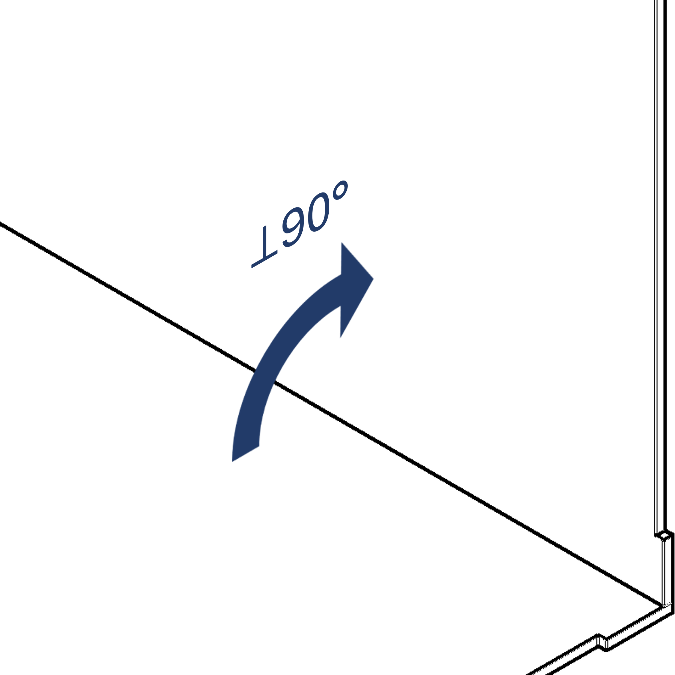
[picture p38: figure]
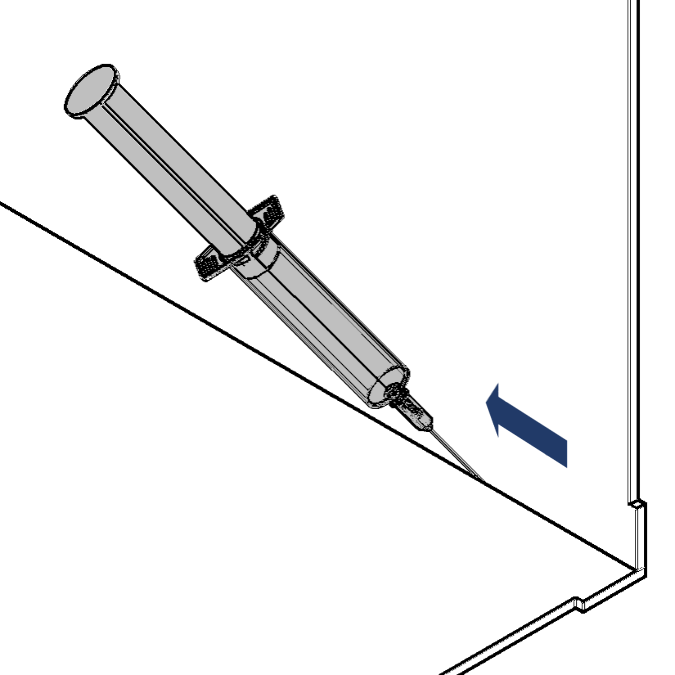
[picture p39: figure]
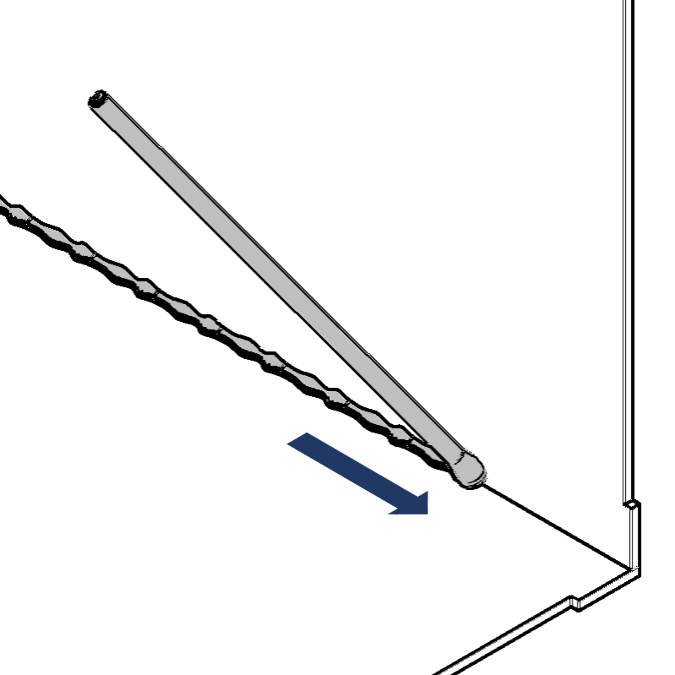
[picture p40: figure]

| ES – Preparación de los screw cubes. Posicione las tuercas en los agujeros hexagonales según correspondan las medidas del agujero. Con una jeringa inyecte resina en las tres muescas para cada tuerca. Aplique luz UV para curar la resina y así queden fijas las tuercas.
| EN – Preparation of the screw cubes. Place the nuts in the hexagonal holes according to the hole dimensions. Using a syringe, inject resin into the three notches for each nut. Apply UV light to cure the resin and secure the nuts in place.

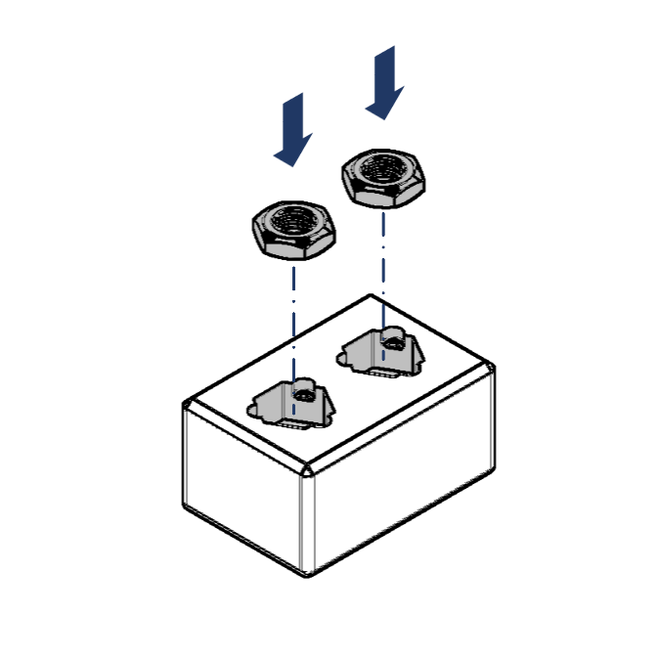
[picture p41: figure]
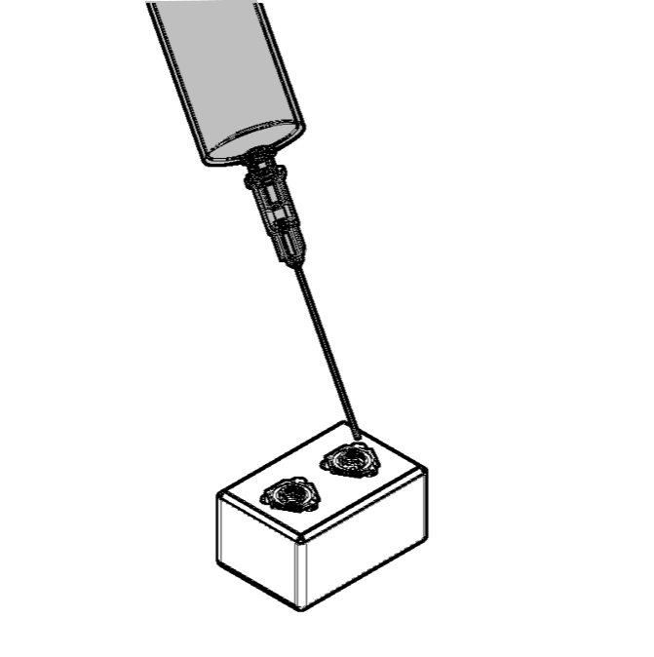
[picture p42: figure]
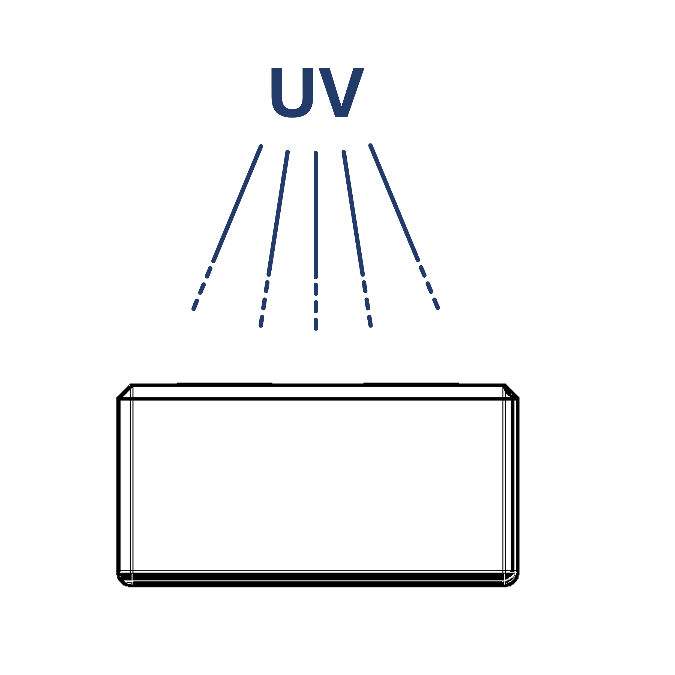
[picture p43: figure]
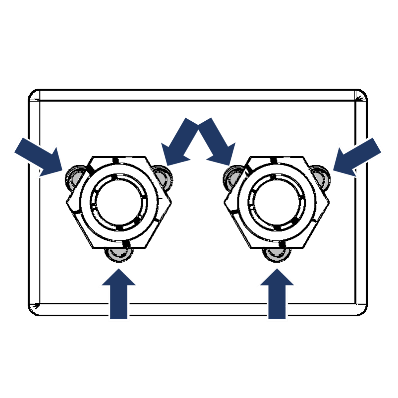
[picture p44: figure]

| | ES – Tenga cuidado con que la resina aplicada solo se inyecte en las muescas indicadas. Evite utilizar resina en exceso que pudiera afectar el hilo de la tuerca.
| | EN – Be careful that the resin applied is only injected into the indicated notches. Avoid using excess resin that could affect the nut thread.

| ES – Pegado de los screw cubes. Aplique pegamento apto para pegar los screw cubes a las paredes de acrilico (como metilmetacrilato). Cubra la superficie de contacto de tal manera que el producto no afecte las tuercas. Posicione el bloque en el lugar de correspondiente aplicando presión mientras se pega adecuadamente.
| EN – Gluing the screw cubes. Apply glue suitable for gluing screw cubes to acrylic walls (such as cyanoacrylate). Cover the contact surface so that the product does not affect the nuts. Position the block in the correct place, applying pressure while gluing it properly.

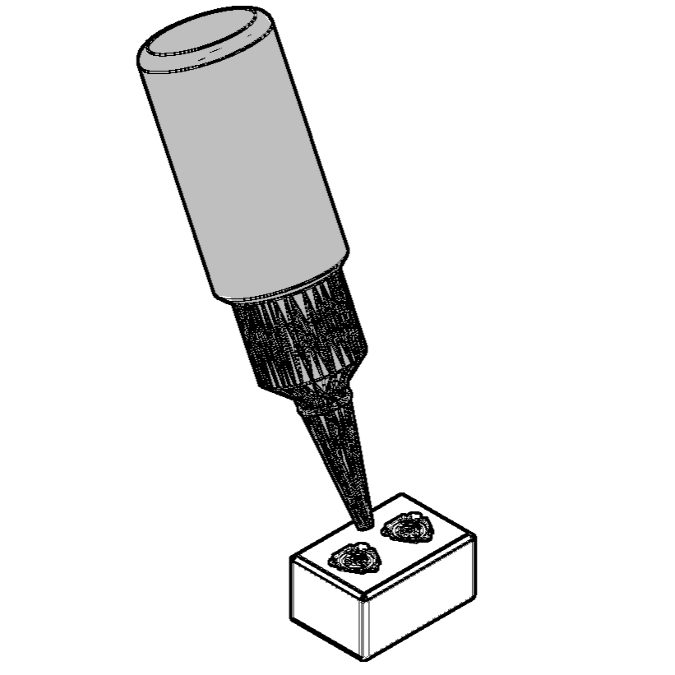
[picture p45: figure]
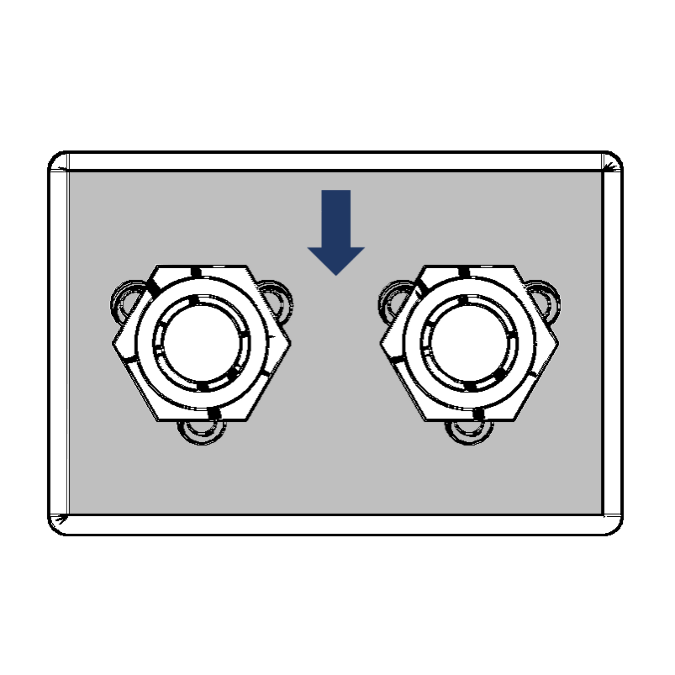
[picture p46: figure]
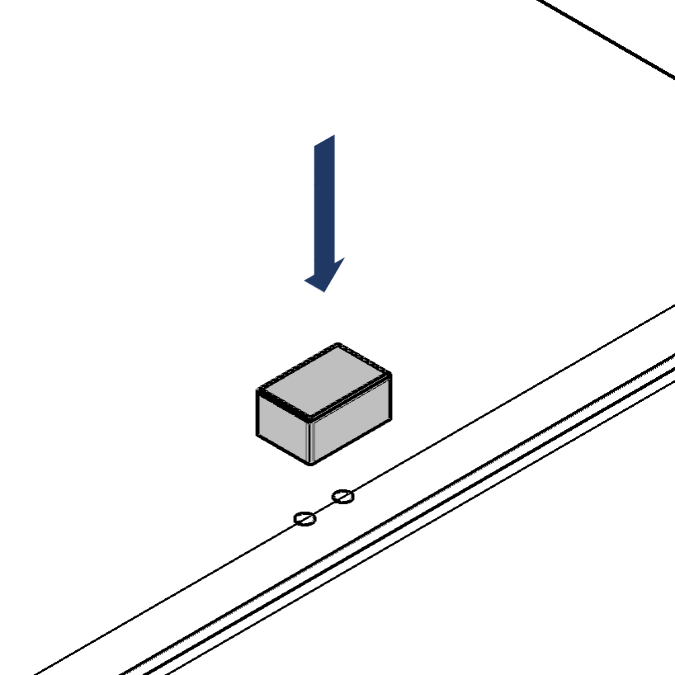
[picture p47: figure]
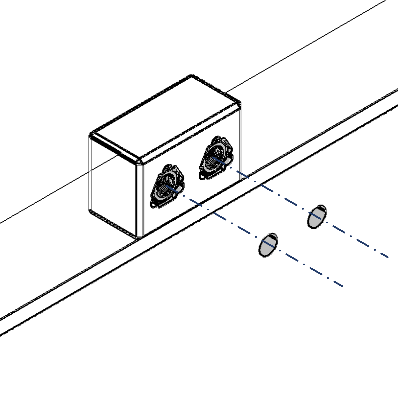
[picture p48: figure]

| | ES – Asegúrese que los agujeros de las paredes coincidan con el eje de las tuercas para que los pernos de fijación entren adecuadamente.
| | EN – Ensure that the holes in the walls match the axis of the nuts so that the fixing bolts fit properly.

| ES – Sellado de los screw cubes y otras piezas anexas. Con una jeringa aplique resina alrededor del perímetro del screw cube de tal manera que el producto se observe de manera continua. Aplique luz UV para curar la resina procurando llegar a cada parte de la unión.
| EN – Sealing screw cubes and other attached parts. Using a syringe, apply resin around the perimeter of the screw cube so that the product is visible continuously. Apply UV light to cure the resin, ensuring that every part of the joint is covered.

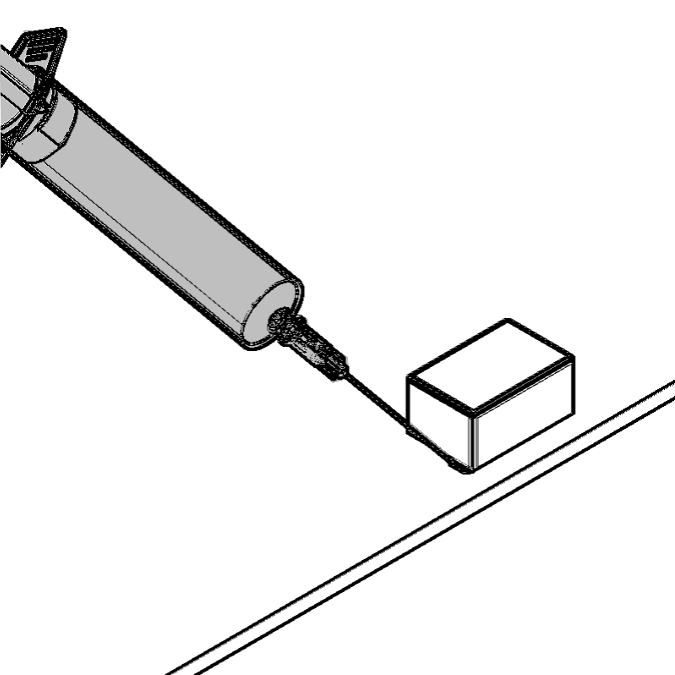
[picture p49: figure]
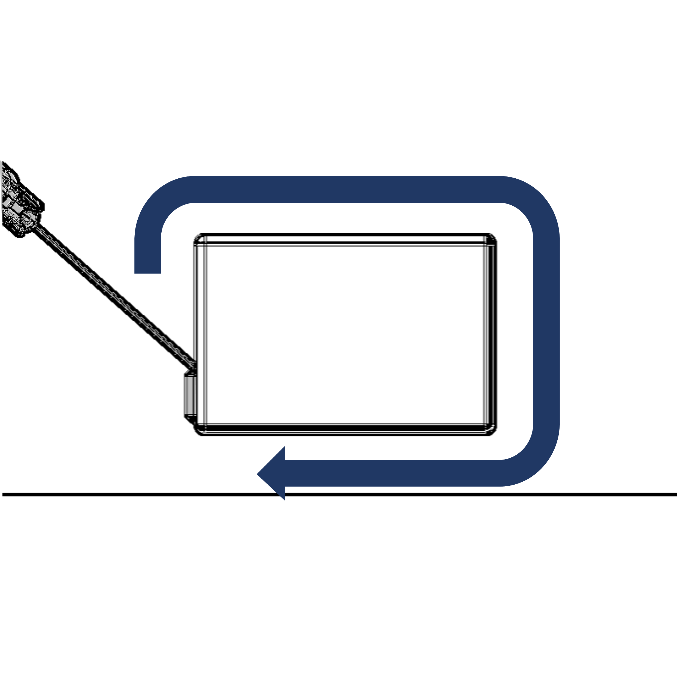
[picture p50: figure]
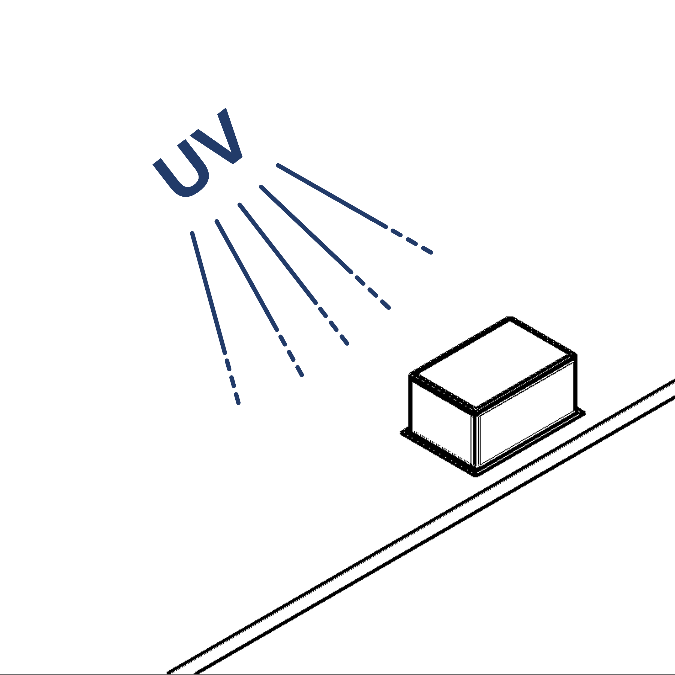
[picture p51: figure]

| | ES – La resina se acumulará en el bisel del bloque por capilaridad. Aplique una cantidad suficiente pero moderada para asegurar el correcto sellado.
| | EN – The resin will accumulate in the chamfer of the block by capillary action. Apply a sufficient but moderate amount to ensure proper sealing.

| Posicionamiento de elementos periféricos. Ubique los distintos elementos en sus posiciones correspondientes y fíjelos con los pernos adecuados (M4, M5 y M6).

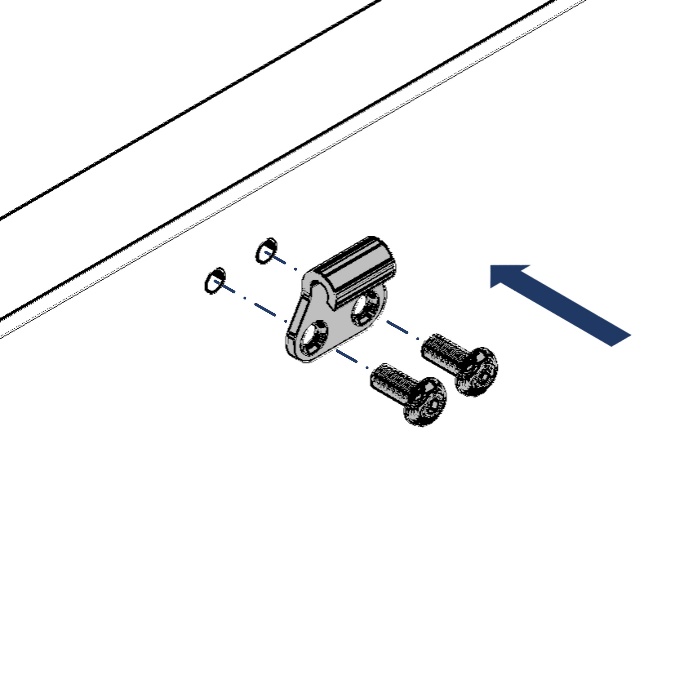
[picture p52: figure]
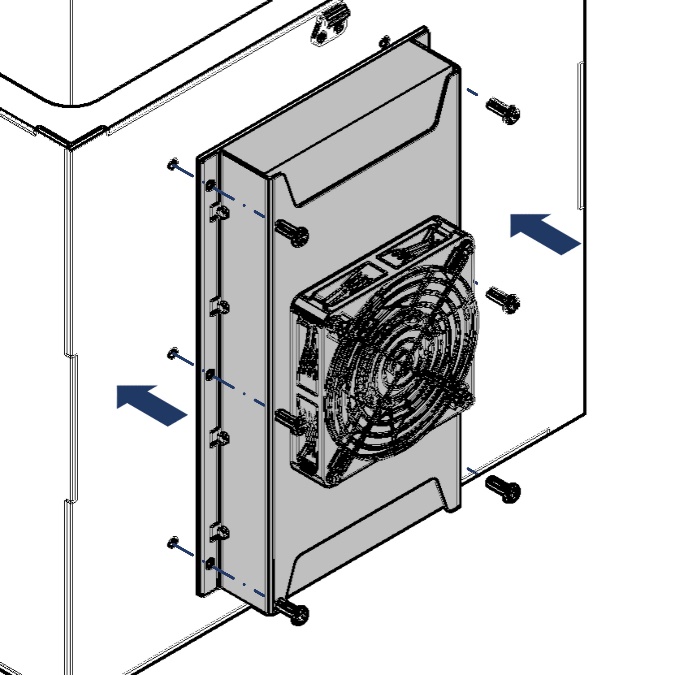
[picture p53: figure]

| Preparación y montaje de cables. Con una herramienta con filo realice cortes en la goma pasa cables para cada uno de los cables que entraran a la incubadora. Pase cada cable a través de la goma. Monte la goma con el marco correspondiente y ajuste los pernos.
| Preparation and installation of cables. Using a sharp tool, make cuts in the cable pass-through rubber for each of the cables that will enter the incubator. Pass each cable through the rubber. Mount the rubber with the corresponding frame and tighten the bolts.

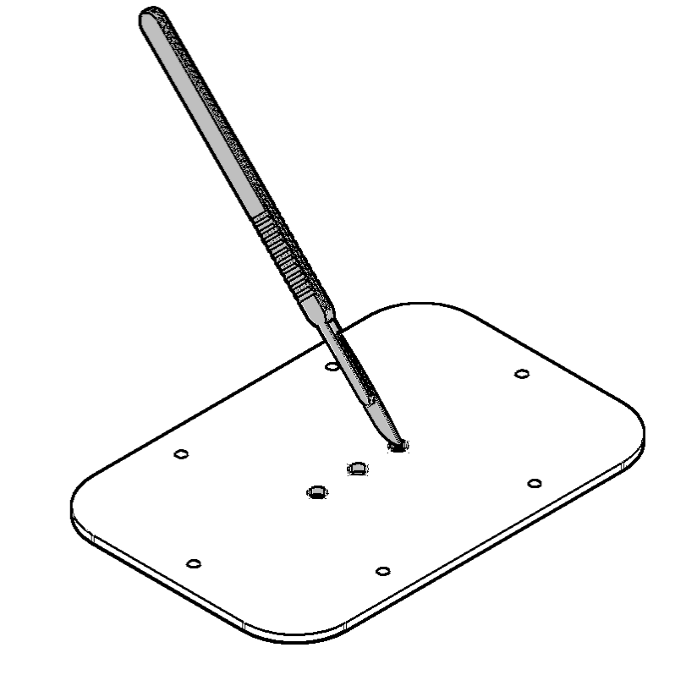
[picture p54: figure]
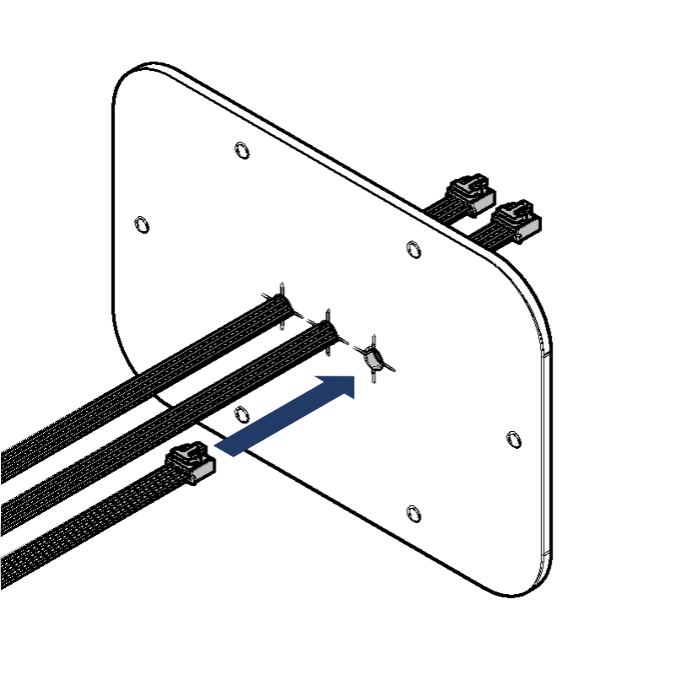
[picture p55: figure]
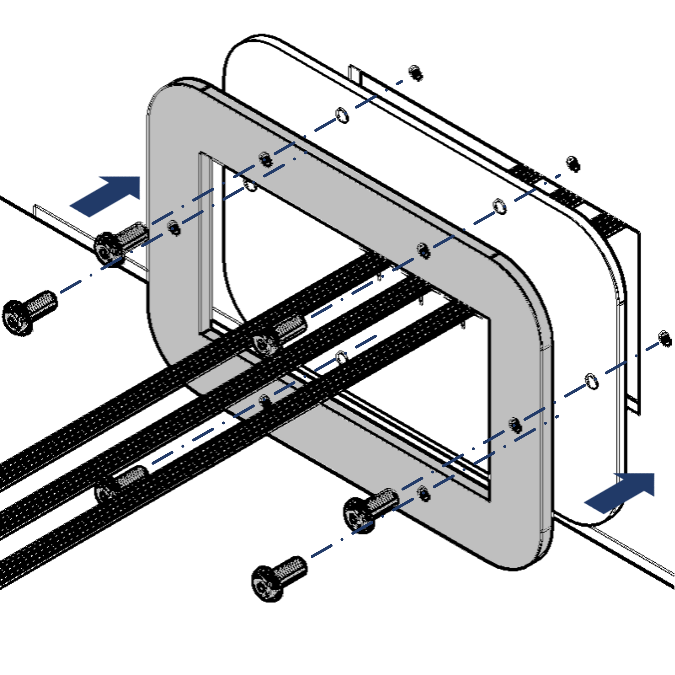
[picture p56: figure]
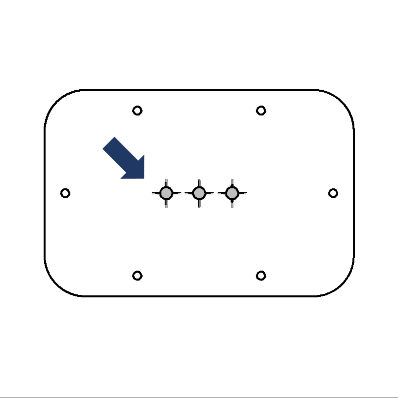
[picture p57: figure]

| | Los cortes para los cables deben ser de tal manera que permitan que cada cable quede rodeado por goma. Es necesario agregar dos cortes perpendiculares que permitan pasar los conectores acoplados a cada cable.

| Cierre de la incubadora. Ubique la empaquetadura de goma sobre el marco de la base de la incubadora. Ponga la tapa sobre la empaquetadura y cierre la incubadora mediate las abrazaderas de cierre rápido.

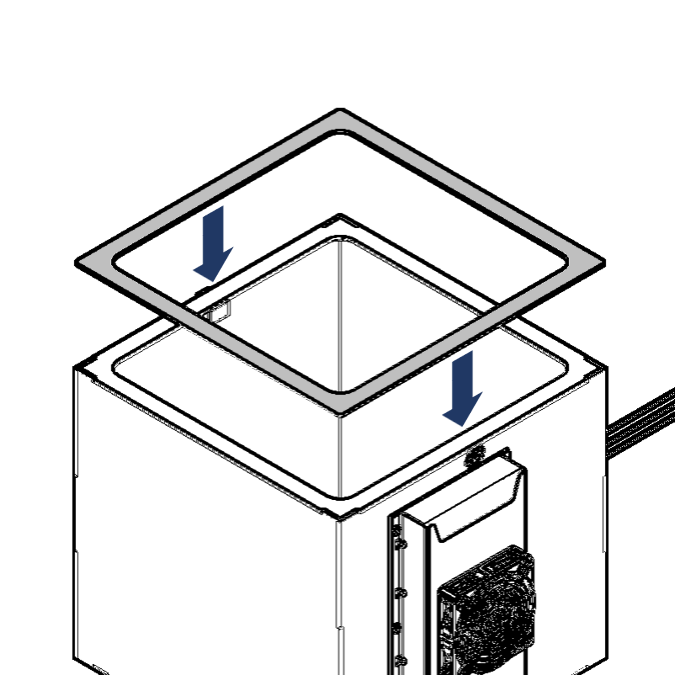
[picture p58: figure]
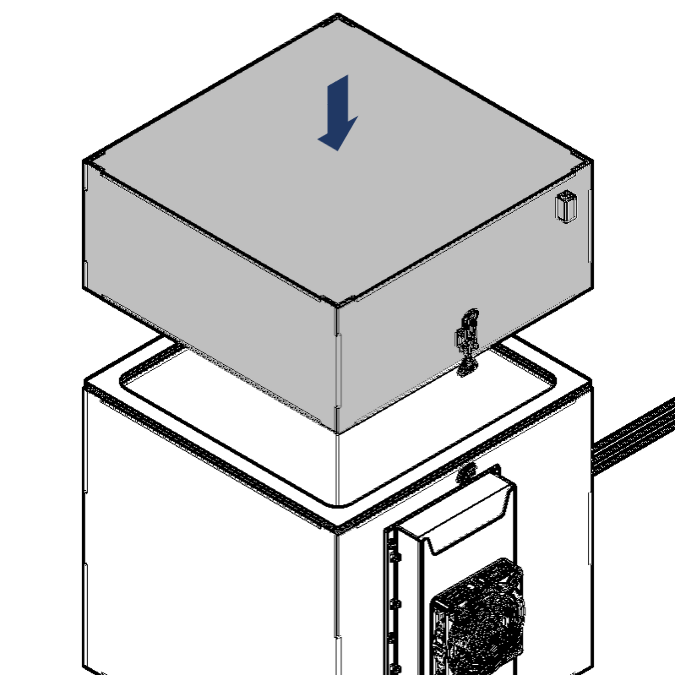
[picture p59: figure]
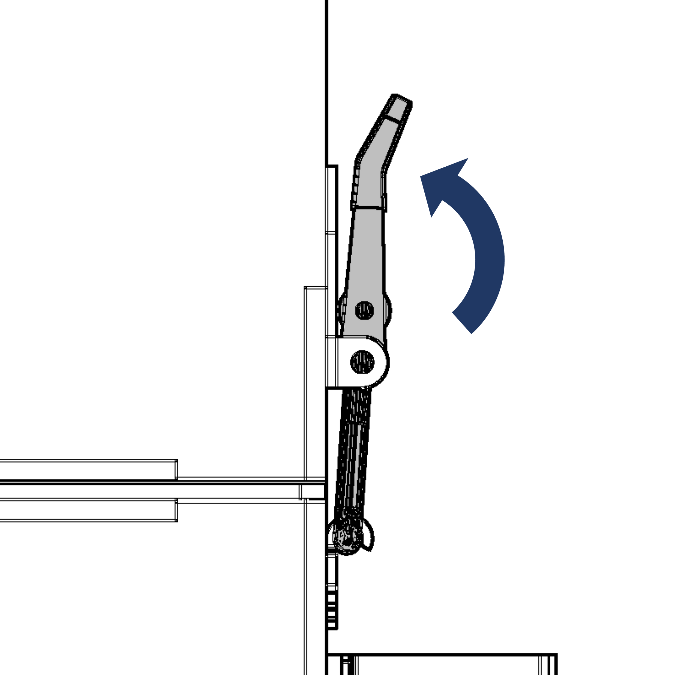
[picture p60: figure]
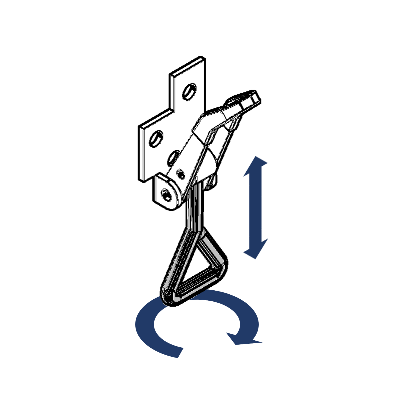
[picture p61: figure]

| | Ajuste el largo de la abrazadera girándola hasta lograr una distancia que permita cerrar la incubadora sin exceder demasiado la tensión.

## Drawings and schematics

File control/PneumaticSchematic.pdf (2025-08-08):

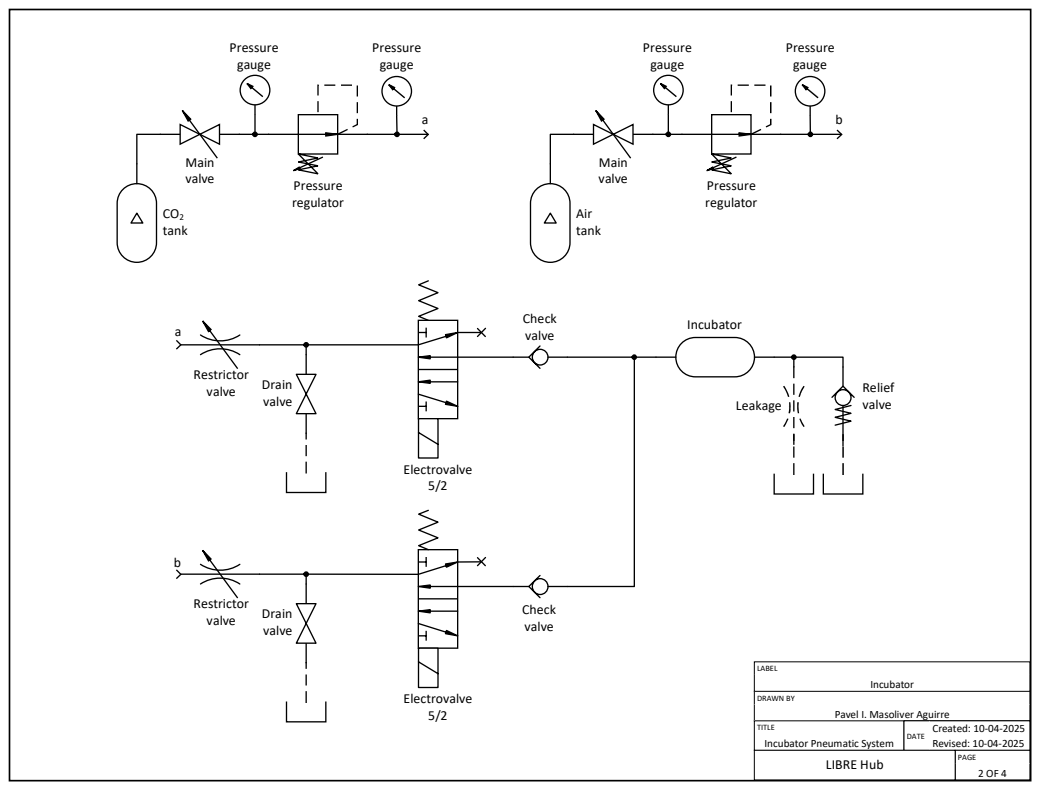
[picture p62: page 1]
DRAWN BY; Pavel I. Masoliver Aguirre; LABEL; IncubatorDATE Created: 10-04-2025; LIBRE Hub; CO2 tank; Main; valve; Pressure; regulator; Pressure gauge; Restrictor; Drain; Electrovalve 5/2; Incubator; Relief; Leakage; Check valve; Air tank

TITLE
Incubator Pneumatic System

Revised: 10-04-2025 PAGE 2 OF 4

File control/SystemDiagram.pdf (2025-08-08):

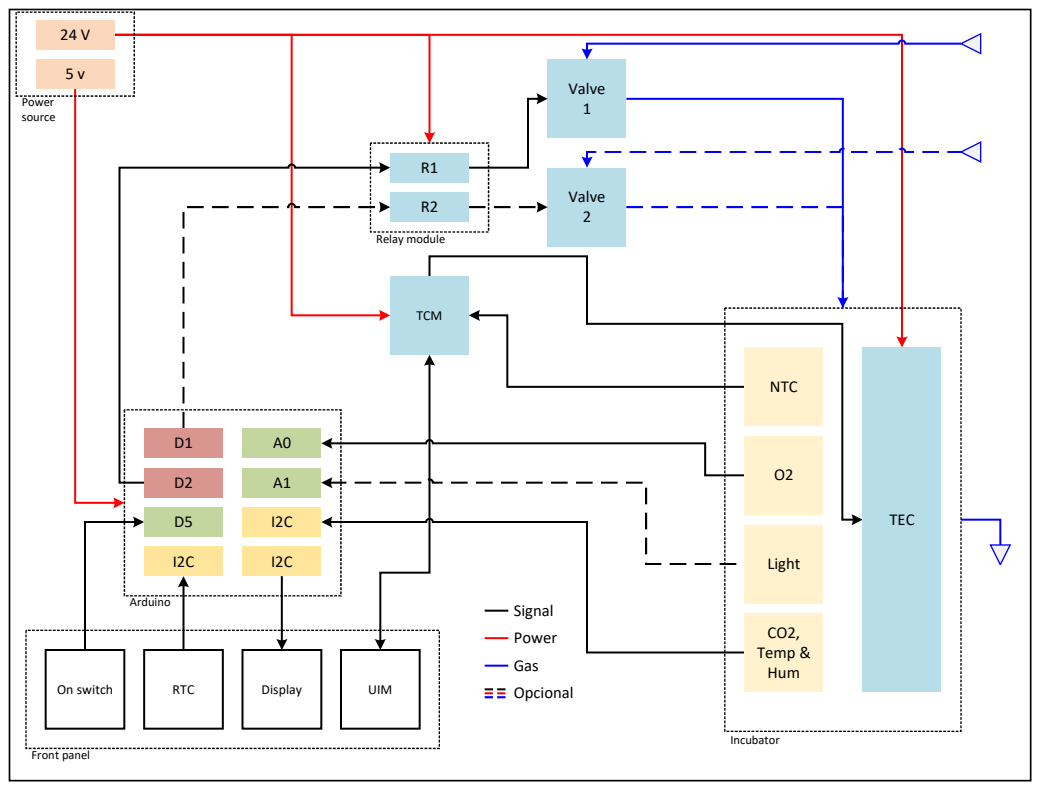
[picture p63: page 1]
Valve 2; Valve 1; TCM; On switch; RTC; Display; UIM; Front panel; Relay module; Signal Power Gas; Power source 24 V; Light; CO2, Temp & Hum; TEC; NTC; Incubator; Opcional; Arduino

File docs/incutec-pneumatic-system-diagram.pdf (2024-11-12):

m

### Pressure

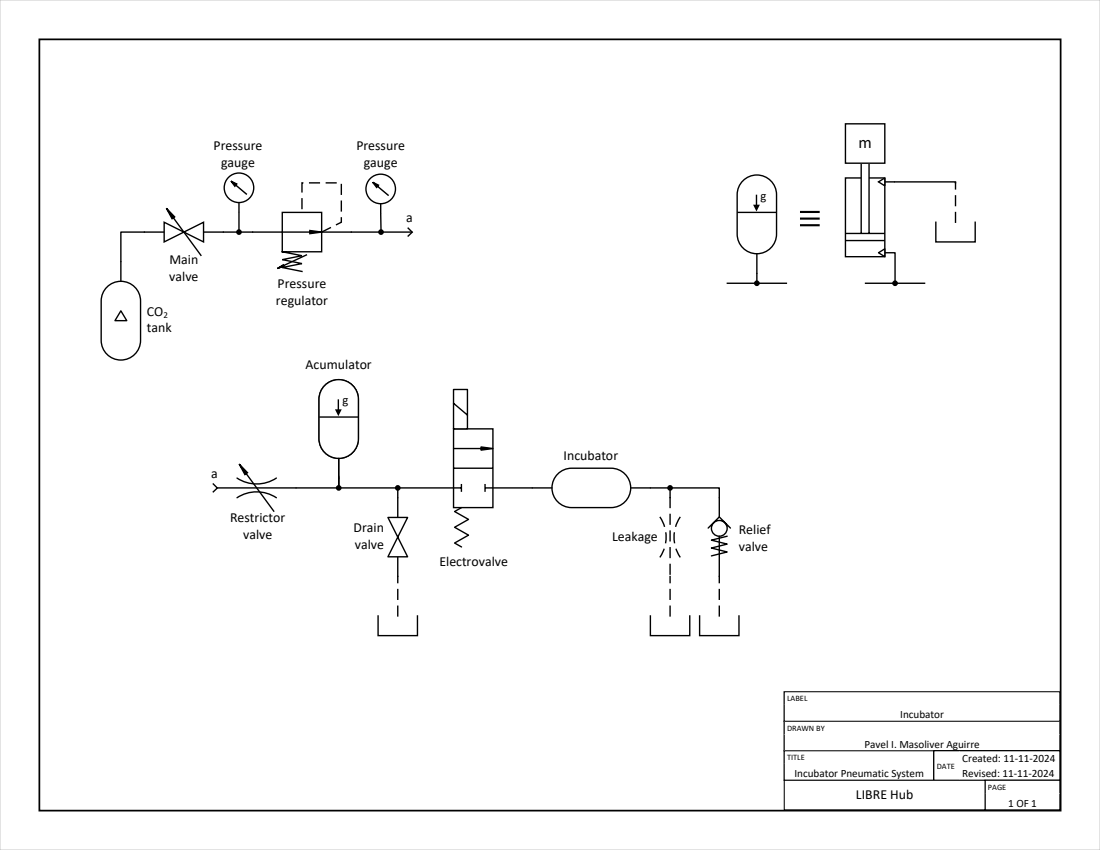
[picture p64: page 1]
DRAWN BY; LABEL; Incubator; DATE; Created: 11-11-2024 Revised: 11-11-2024; PAGE; LIBRE Hub; CO2 tank; Main; valve; Pressure; regulator; gauge; Pressure gauge; Restrictor valve; Acumulator; Drain valve; Electrovalve; Relief valve; Leakage

Pavel I. Masoliver Aguirre

TITLE
Incubator Pneumatic System

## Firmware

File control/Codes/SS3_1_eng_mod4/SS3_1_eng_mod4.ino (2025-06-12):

/*
    SS3_eng.ino
    Control programm for an anaerobic box
    Copyright (c) 2020 Achim Herrmann
    Author     : Achim Herrmann
    Create Time: October 2020
    Change Log :
    The MIT License (MIT)
    Permission is hereby granted, free of charge, to any person obtaining a copy
    of this software and associated documentation files (the "Software"), to deal
    in the Software without restriction, including without limitation the rights
    to use, copy, modify, merge, publish, distribute, sublicense, and/or sell
    copies of the Software, and to permit persons to whom the Software is
    furnished to do so, subject to the following conditions:
    The above copyright notice and this permission notice shall be included in
    all copies or substantial portions of the Software.
    THE SOFTWARE IS PROVIDED "AS IS", WITHOUT WARRANTY OF ANY KIND, EXPRESS OR
    IMPLIED, INCLUDING BUT NOT LIMITED TO THE WARRANTIES OF MERCHANTABILITY,
    FITNESS FOR A PARTICULAR PURPOSE AND NONINFRINGEMENT. IN NO EVENT SHALL THE
    AUTHORS OR COPYRIGHT HOLDERS BE LIABLE FOR ANY CLAIM, DAMAGES OR OTHER
    LIABILITY, WHETHER IN AN ACTION OF CONTRACT, TORT OR OTHERWISE, ARISING FROM,
    OUT OF OR IN CONNECTION WITH THE SOFTWARE OR THE USE OR OTHER DEALINGS IN
    THE SOFTWARE.
*/

#include "Wire.h"
#include "DS1307.h"               // Real clock module library
DS1307 clock;                    
#include <SD.h>                   // SD library
#include <SPI.h>                  // SPI communication library for SD card
#include <SeeedOLED.h>            // Oled display libraey
#include "SCD30.h"                // SCD30 library

//SCD30
#if defined(ARDUINO_ARCH_AVR)
    #pragma message("Defined architecture for ARDUINO_ARCH_AVR.")
    #define SERIAL Serial
#elif defined(ARDUINO_ARCH_SAM)
    #pragma message("Defined architecture for ARDUINO_ARCH_SAM.")
    #ifdef SEEED_XIAO_M0
        #define SERIAL Serial
    #elif defined(ARDUINO_SAMD_VARIANT_COMPLIANCE)
        #define SERIAL SerialUSB
    #else
        #define SERIAL Serial
    #endif
#elif defined(ARDUINO_ARCH_SAMD)
    #pragma message("Defined architecture for ARDUINO_ARCH_SAMD.")
    #ifdef SEEED_XIAO_M0
        #define SERIAL Serial
    #elif defined(ARDUINO_SAMD_VARIANT_COMPLIANCE)
        #define SERIAL SerialUSB
    #else
        #define SERIAL Serial
    #endif
#elif defined(ARDUINO_ARCH_STM32F4)
    #pragma message("Defined architecture for ARDUINO_ARCH_STM32F4.")
    #ifdef SEEED_XIAO_M0
        #define SERIAL Serial
    #elif defined(ARDUINO_SAMD_VARIANT_COMPLIANCE)
        #define SERIAL SerialUSB
    #else
        #define SERIAL Serial
    #endif
#else
    #pragma message("Not found any architecture.")
    #define SERIAL Serial
#endif

//control parameters
const float co2set = 2;                               // CO2 concentration setting
const int co2period = 20;                             // CO2 injection period, x co2period times 3 seconds
const int co2gastime = 50;                            // CO2 injection time, in miliseconds
const float oxset = 0.40;                             // O2 setting
const float humset = 85;                              // Humidity setting
const float tempset = 27;                             // Temperature setting

const float OxMaxSoll = 0.40;                         // maximum of 02 before gasing (N2/H2)v
const byte GasFlowChamberDuration = 10;               // How long should be gased after detecting over OX (N2/H2)
const byte HumSoll = 85;                              // maximum of humidity before gasing (N2)
const byte HumDuration = 10;                          // How long should be gased after detecting humidity over HumSoll(N2)
boolean StdON = true;                                 // true for hourly gasing ON, set false for OFF

//H2 SetUp
const float R0 = 3.8;                                 // Resting resistance of H2 Sensors. Determine by using "H2 setup"
const int H2Pin = A2;                                 // PIN used for the H2 sensor
float H2ratio = 0;
const float H2soll = 0.15;                            // Minimum amount before automatic feeding of H2 containing gas
const int GasFlowSchleuseDuration = 300;              // How long should the air lock be gased (s)

//Display setUP
char line0[17];                                       // first line in Oled display: Temperature
char line1[17];                                       // second line in Oled display: Relative Humidity
char line2[17];                                       // third line in Oled display: Oxygen%
char line3[17];                                       // fourth line in Oled display: H2 indicator
char line4[17];                                       // fifth line in Oled display: CO2 concentration
char line5[17];                                       // sixth line in Oled display: Status of controller
char line6[17];                                       // seventh line in Oled display: (SD) errorcodes
byte TimeLine = 7;                                    // eight line in Oled display: date
boolean timeDisplayIni = false;                       // 0 declares dots have to be rewriten for time display

//O2 SetUP
const float VRefer = 3.3;                             // voltage of connected to the O2 sensor
const int pinAdc   = A0;                              // PIN used for the O2 sensor
float OxVout =0;
const int numReadings = 10;                           // Average of number of readings
float readings[numReadings];                          // single sensor readings
int OxReadIndex = 0;                                  // Index of current reading
float OxTotal = 0;                                    // running total
float OxAverage = 0;                                  // average of readings so far
float OxValue = 0;                                    // Oxygen in %
int GasFlowChamberTimer = 0;

//Humidity SetUp
float humidity = 0;
boolean HumControl = false;                           // initial state of the controller
int HumTimer = 0;

//Temperature setup
float temper = 0;

//CO2 setup
float co2general = 100;                               // Registra la concentración de CO2, inicializa en 100%
int counter = 0;

//SD SetUp
const int ChipSelect = 4;                             // Pin mounting the SD-Card
File mySD;                                            // variable for working with file object
boolean SdUberschrift = false;
byte SdWriteFrequenzy = 1;                            // How frequent a reading is saved ( 0 = 60 per minute; 59 = 1 per minute)

//General setup
int interruptor = 2;                                  // Switch pin
int rele = 3;                                         // Relay pin

//TIMING
byte TaktS = 0;                                       // count seconds till 60
byte TaktM = 0;                                       // count minutes till 60

//Steuerung                                           // PINs connecting to external equipment
const byte GasChamber = 5;                            // PIN relay switch for gas in chamber  
const byte GasSchleuse = 6;                           // PIN relay switch for gas in Airlock
const byte Schalter = 7;                              // PIN switch for on/off
const byte KillSwitch = 8;                            // PIN for changing gasing modes
boolean GasFlowChamber = false;
boolean GasFlowSchleuse = false;
int GasFlowSchleuseTimer = 0;
double GasFreq = -10000;                              // Variables for automatic shutdown of gasing
byte GasERROR;
boolean GasOverride = false;
boolean GasSchleuseStatus = false;
String Override = "GAS OVERRIDE!   ";                 // Shows status of Killswitch on Display
boolean GasFlowChamberSwitch = false;
boolean GasSchleuseWaitReset = false;
const int SicherheitsIntervall = 10000;               // Minimum expected time between gasing caused by high O2 or low H2 during normal oppperation
byte GasERRORLimit = 5;                               // Limit for how often this interval between gasings can be breached in sucsesion before error
byte tOLD;                                            // How often gasing happens per hour
boolean BegasungBuffer;
byte BegasungH;
boolean StdBegasung = false;                          // Controls the hourly gasing

void setup(){  
  Serial.begin(115200);                               // start serial for output
  delay(150);
  /* Power up,delay 150ms,until voltage is stable */
  Wire.begin();
  delay(600);
  
  clock.begin();
  delay(100);
  
  scd30.initialize();                                 // Initialize CO2, Temp, Hum sensor
  SeeedOled.init();                                   // initialze SEEED OLED display
  SeeedOled.setNormalDisplay();                       // Set display to normal mode (i.e non-inverse mode)
  SeeedOled.setPageMode();                            // Set addressing mode to Page Mode  
  SeeedOled.clearDisplay();                           // cleares the display
  
  pinMode(10,OUTPUT);                                 // Pin 10 is reserved for SD card; DONT USE
  SD.begin(ChipSelect);

  pinMode(GasChamber, OUTPUT);                        // Pins for Relays and Switches
  pinMode (GasSchleuse, OUTPUT);
  pinMode(Schalter, INPUT);
  pinMode(KillSwitch, INPUT);
  digitalWrite(KillSwitch, HIGH);

  pinMode(interruptor,INPUT);                         // Switch pin setting
  pinMode(rele,OUTPUT);                               // Relay pin setting


  //ONLY USE ONCE TO SET UP CLOCK!!!!
  /*clock.fillByYMD(2025,5,29);        //Jan 19,2019
   clock.fillByHMS(10,28,00);          //10:27 00"
   clock.fillDayOfWeek(TUE);          //Saturday
   clock.setTime(); */               //write time to the RTC chip
  tOLD = clock.hour;

  for (int thisReading = 0; thisReading < numReadings; thisReading++){
  readings[thisReading] = 0;
  }
}
//---------------------------------------------------------------------------------------------------------------
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

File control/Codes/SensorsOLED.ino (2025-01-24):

/*
    basic_demo.ino
    Example for MCP9600

    Copyright (c) 2018 Seeed Technology Co., Ltd.
    Website    : www.seeed.cc
    Author     : downey
    Create Time: May 2018
    Change Log :

    The MIT License (MIT)

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
    THE SOFTWARE IS PROVIDED "AS IS", WITHOUT WARRANTY OF ANY KIND, EXPRESS OR
    IMPLIED, INCLUDING BUT NOT LIMITED TO THE WARRANTIES OF MERCHANTABILITY,
    FITNESS FOR A PARTICULAR PURPOSE AND NONINFRINGEMENT. IN NO EVENT SHALL THE
    AUTHORS OR COPYRIGHT HOLDERS BE LIABLE FOR ANY CLAIM, DAMAGES OR OTHER
    LIABILITY, WHETHER IN AN ACTION OF CONTRACT, TORT OR OTHERWISE, ARISING FROM,
    OUT OF OR IN CONNECTION WITH THE SOFTWARE OR THE USE OR OTHER DEALINGS IN
    THE SOFTWARE.
*/

#include "Seeed_SHT35.h"
#include <SeeedOLED.h>
#include <Wire.h>


/*SAMD core*/
#ifdef ARDUINO_SAMD_VARIANT_COMPLIANCE
    #define SDAPIN  20
    #define SCLPIN  21
    #define RSTPIN  7
    #define SERIAL SerialUSB
#else
    #define SDAPIN  A4
    #define SCLPIN  A5
    #define RSTPIN  2
    #define SERIAL Serial
#endif

SHT35 SHTsensor(SCLPIN);


//H2 SetUp
const float R0 = 5.55;           // resting voltage of H2 Sensors; Determine by using "H2 setup"
const int H2Pin = A2;           // PIN used for the H2 sensor
float H2ratio = 0;
const float H2soll = 0.15;      // minimum amount before automatic feeding of H2 containing gas
const int GasFlowSchleuseDuration = 300;                      // How long should the air lock be gased (s)

//Display setUP
char line0[17];                 // first line in Oled display: Temp
char line1[17];                 // second line in Oled display: rH
char line2[17];                 // third line in Oled display: Oxygen%
char line3[17];                 // fourth line in Oled display: H2 indicator
char line4[17];                 // fifth line in Oled display: PAR
char line5[17];                 // sixth line in Oled display: Status of controller
char line6[17];                 // seventh line in Oled display: (SD) errorcodes
byte TimeLine = 7;              // eight line in Oled display: datu
boolean timeDisplayIni = false;

//O2 SetUP
const float VRefer = 3.3;       // voltage of connected to the O2 sensor
const int pinAdc   = A0;        // PIN used for the O2 sensor
float OxVout =0;
const int numReadings = 10;     // Average of number of readings
float readings[numReadings];    // single sensor readings
int OxReadIndex = 0;            // Index of current reading
float OxTotal = 0;              // running total
float OxAverage = 0;            // average of readings so far
float OxValue = 0;              // Oxygen in %
int GasFlowChamberTimer = 0;


void setup() {
    Wire.begin();
    SERIAL.begin(115200);
    delay(10);
    SERIAL.println("serial start!!");
    //if (SHTsensor.init()) {
    //    SERIAL.println("sensor init failed!!");
    //}
    SeeedOled.init();                                                       // Initialze SEEED OLED display
    SeeedOled.setNormalDisplay();                                           // Set display to normal mode (i.e non-inverse mode)
    SeeedOled.setPageMode();                                                // Set addressing mode to Page Mode  
    SeeedOled.clearDisplay(); 
    delay(1000);
}


void loop() {

  float temp, hum;
  SHTsensor.read_meas_data_single_shot(HIGH_REP_WITH_STRCH, &temp, &hum);   // Get temperature and humidity

//Temperature
  String tDisplay = F("Temp ");
  if(temp <-10 || temp >80){
    tDisplay = tDisplay + F("RANGE ERROR");
    }
    else{
      char tBuff[6]; 
      dtostrf(temp, 5, 2, tBuff);                         
      tDisplay = tDisplay + tBuff + " *C";
      }

  for(int i=0;i<17;i++){
    line0[i]=tDisplay[i];
    }
   
//Humidity 
  String rhDisplay = F("Hum");            
  if(hum < 0){                                                // If hum is close to 0 or 100% displays error
    rhDisplay = rhDisplay + F("  RANGE LOW");
    }
    else if(hum >= 100){
      rhDisplay = rhDisplay + F("  RANGE HIGH");
      }
      else{
        char rhBuff[6];                                                      
      dtostrf(hum, 5, 2, rhBuff);                             // Creates a string lenght 5, decimals 2 and name rhBuff
      rhDisplay = rhDisplay +"  "+ rhBuff + F(" %");     
      }

  for(int i=0;i<17;i++){
    line1[i]=rhDisplay[i];                                    // Humidity string
    }

//Oxygen
  float OxValue = readConcentration();
  String OxDisplay= F("OxLvl");
  if (OxValue < 10){
     OxDisplay = OxDisplay + "  ";
     }
     else{
     OxDisplay = OxDisplay + ' ';
     }

  char OxBuff[6];                                              
  dtostrf(OxValue, 5, 2, OxBuff);                             // Creates a string lenghte 5, decimals 2 and name OxBuff      
  OxDisplay = OxDisplay + OxBuff + " %";
  for(int i=0;i<17;i++){
    line2[i]=OxDisplay[i];                                    // Oxygen concentration string
    }
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

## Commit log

2024-12-19 Reference code and sensor datasheets.
2025-01-24 OLED sensors display and system diagram
2025-03-13 CO2 sensor datasheet added
2025-06-12 Incubator control and h2 sensor setup codes
2025-08-08 Control images actualization. 3D model update.
    [Incubator - Part 1 (1).step, Incubator - Part 1 (10).step, Incubator - Part 1 (11).step, Incubator - Part 1 (12).step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]
2025-09-10 New control code and assembly images
2025-09-22 Assembly images actualization
2025-09-22 More assembly images
2025-09-25 Assembly iamage correction and steps document
2025-09-30 File name correction
    [IncubatorPart0.step, IncubatorPart1.step, IncubatorPart10.step, IncubatorPart11.step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]
2025-10-07 Page update
    [ScrewCube_4mm.stl]
2025-10-07 stl models and page update
    [ScrewCubeLock1.stl, ScrewCubeLock2.stl, ScrewCube_5mm.stl, ScrewCube_6mm.stl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]
2025-10-08 More incubator stl files
    [Base.stl, BaseBack.stl, BaseFront.stl, BaseSide1.stl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]
